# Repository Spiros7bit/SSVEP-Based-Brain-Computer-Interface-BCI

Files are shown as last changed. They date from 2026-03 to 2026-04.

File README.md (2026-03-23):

# SSVEP-Based Brain-Computer Interface

## Overview

This project implements a real-time Steady-State Visually Evoked Potential (SSVEP) Brain-Computer Interface (BCI) using an ESP32 microcontroller and a custom PCB for analog interface. It was developed as part of a thesis and demonstrates how EEG signals can be processed and classified in real time on embedded hardware.

The system detects brain responses to visual stimuli at specific frequencies and converts them into control decisions.

---

## System Architecture

The signal processing pipeline consists of the following stages:

1. **Analog Interface**
   
   * Instrumentation Amplifier
   * Low Pass Filter, Sallen Key, 2 order
   * AC amplifier
   * Notch 50 Hz filter
   * Final AC Amplifier
   * Right Leg Driver circuit
     
3. **Signal Acquisition**

   * ADC sampling at 1 kHz
   * Hardware timer interrupt for precise timing

4. **Preprocessing**

   * DC offset removal (IIR high-pass filter)
   * FIR band-pass filtering

5. **Feature Extraction**

   * Goertzel algorithm for frequency detection
   * Target frequencies: 10 Hz, 12 Hz, 20 Hz, 24 Hz

6. **Decision Making**

   * Argmax power comparison
   * Median Absolute Deviation (MAD)-based classifier

7. **Output**

   * Real-time signal visualization via Serial Plotter
   * Classification results (Argmax & MAD)

---

## Features

* Analog interface and Acquition System
* Real-time processing on ESP32
* 1 kHz sampling using hardware timer interrupts
* Efficient fixed-point DSP implementation
* FIR filtering with circular buffer
* Sliding window Goertzel analysis (with overlap)
* Robust classification using MAD
* Serial output for debugging and visualization

---

## Hardware Requirements

* ESP32 development board
* EEG acquisition circuit (as designed in the thesis)
* Electrodes and analog front-end

**ADC Input:** GPIO34 (ADC1_CHANNEL_6)

---

## Software Requirements

* Arduino IDE or PlatformIO
* ESP32 board support package

---

## How It Works

### Sampling

A hardware timer triggers ADC sampling at 1000 Hz. Each sample is processed in real time.

### DC Removal

A simple IIR filter removes the DC component from the signal:

```
dc_est = dc_est + k * (x - dc_est)
```

### FIR Filtering

A band-pass FIR filter is applied to isolate relevant EEG frequencies.

### Goertzel Algorithm

The Goertzel algorithm is used to compute the energy at specific target frequencies efficiently.

* Window size: 2048 samples
* Step size: 256 samples (overlap processing)

### Decision Logic

Two decision methods are implemented:

1. **Argmax**

   * Compares power between frequency groups

2. **MAD (Median Absolute Deviation)**

   * Computes a robust threshold based on signal statistics
   * Reduces noise and false detections

---

## Output Format

The system outputs data via Serial in the following format:

```
signal_value, argmax_decision, mad_decision
```

This can be visualized using the Arduino Serial Plotter.

---

## Project Structure

```
.
├── main.ino
├── fir_new_2_1000hz.h   # FIR filter coefficients
├── README.md
```

---

## Applications

* Brain-computer interfaces (BCI)
* Assistive technologies
* Neuroengineering research
* Real-time embedded DSP systems

---

## Future Improvements

* Add more target frequencies
* Improve classification accuracy
* Wireless data transmission (Bluetooth/WiFi)
* GUI for real-time monitoring
* Add a TinyML algorithm

---

## Author

Developed as part of a thesis project on SSVEP-based Brain-Computer Interfaces.

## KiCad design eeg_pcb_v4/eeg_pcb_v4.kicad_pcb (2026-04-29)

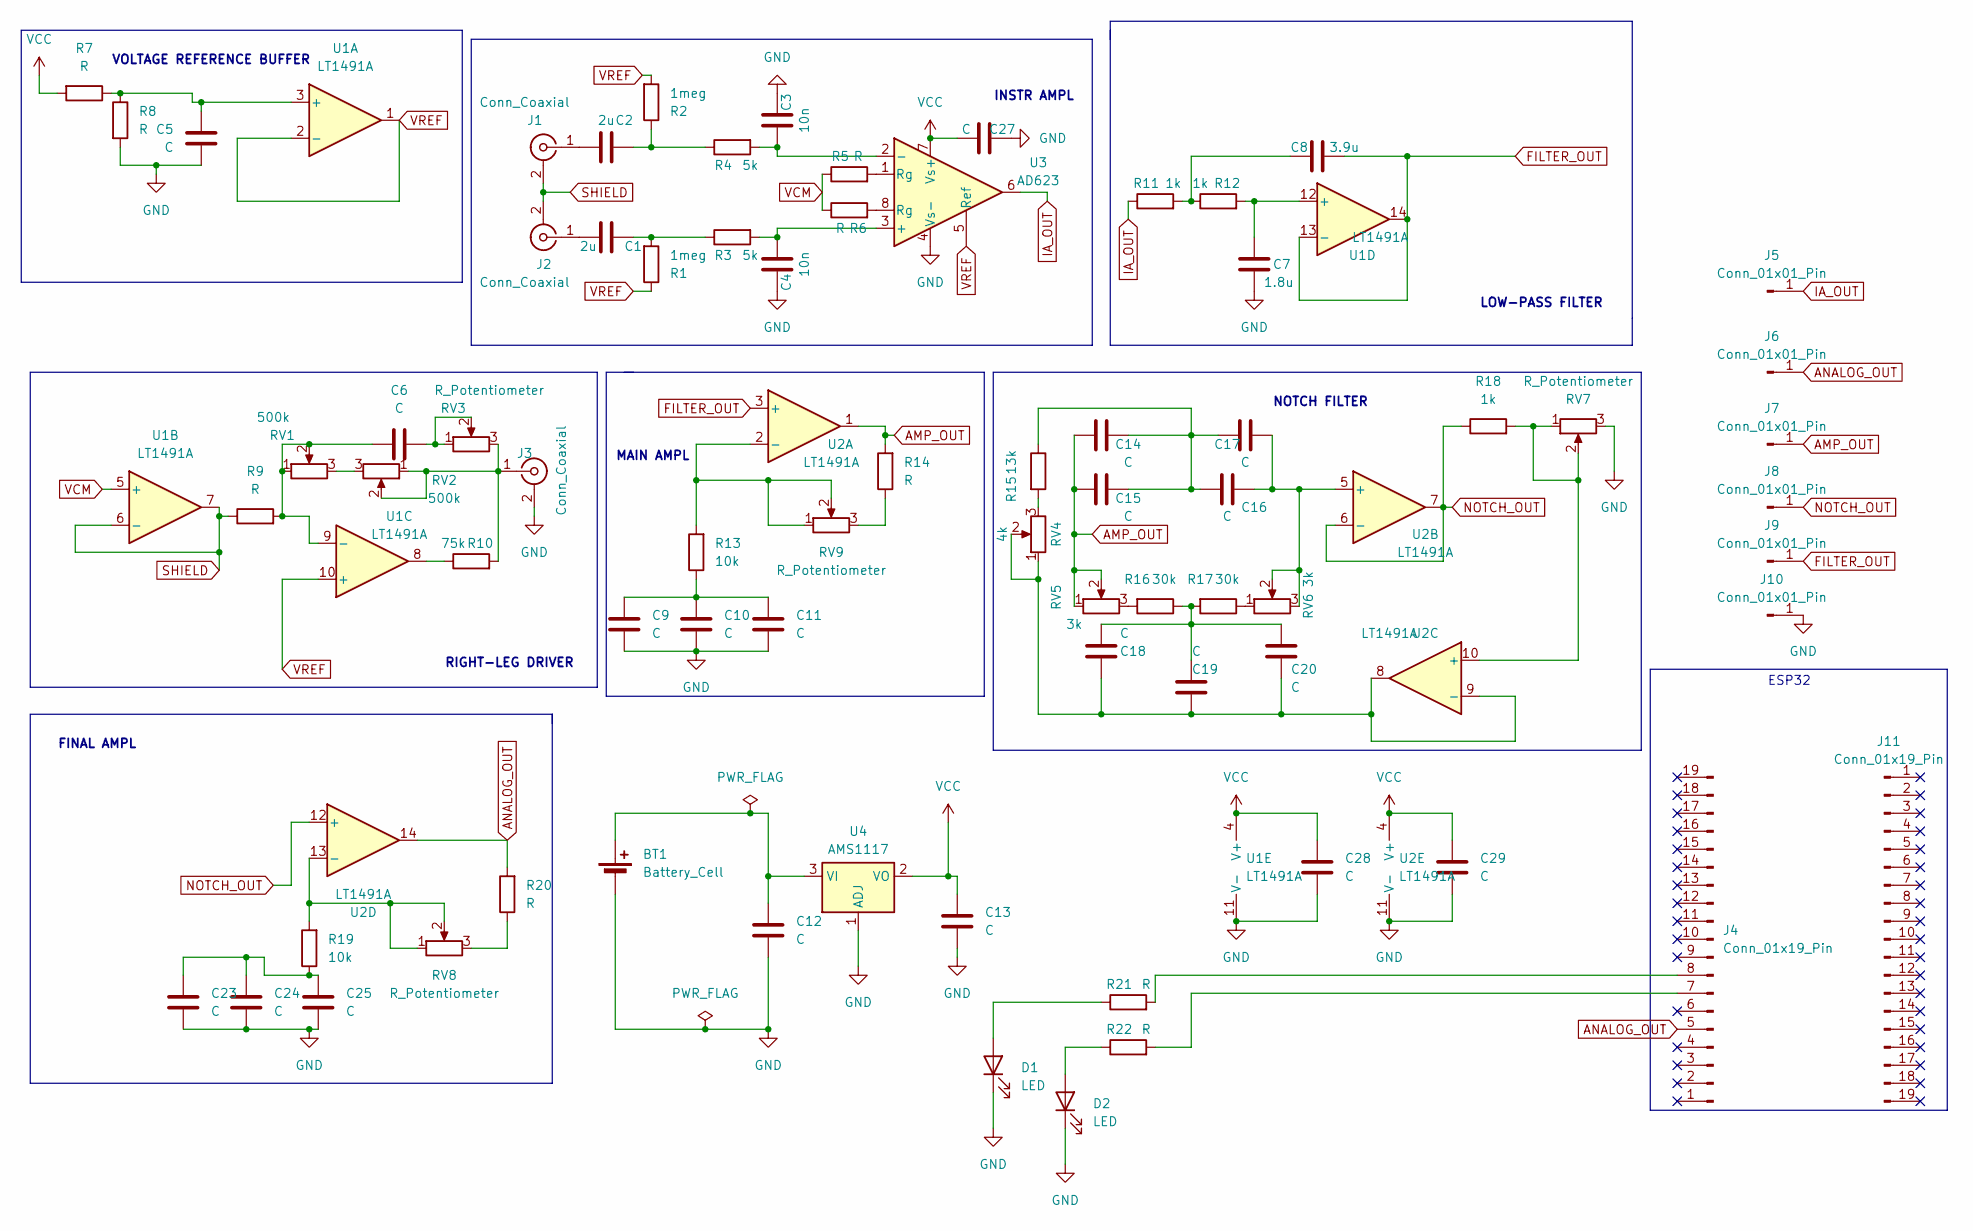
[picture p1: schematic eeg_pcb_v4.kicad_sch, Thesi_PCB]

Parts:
BT1: Battery_Cell; TerminalBlock_Altech_AK300-2_P5.00mm
C1, C2: 2u; C_1206_3216Metric
C3, C4: 10n; C_1206_3216Metric
C5, C6, C9, C10, C11, C12, C13, C14, C15, C16, C17, C18, C19, C20, C23, C24, C25, C27, C28, C29: C; C_1206_3216Metric
C7: 1.8u; C_1206_3216Metric
C8: 3.9u; C_1206_3216Metric
D1, D2: LED; LED_0805_2012Metric
J1, J2, J3: Conn_Coaxial; BNC_Amphenol_B6252HB-NPP3G-50_Horizontal
J4, J11: Conn_01x19_Pin; PinHeader_1x19_P2.54mm_Vertical
J5, J6, J7, J8, J9, J10: Conn_01x01_Pin; TestPoint_Pad_D1.0mm
R1, R2: 1meg; R_1206_3216Metric
R3, R4: 5k; R_1206_3216Metric
R5, R6, R7, R8, R9, R14, R20, R21, R22: R; R_1206_3216Metric
R10: 75k; R_1206_3216Metric
R11, R12, R18: 1k; R_1206_3216Metric
R13, R19: 10k; R_1206_3216Metric
R15: 13k; R_1206_3216Metric
R16, R17: 30k; R_1206_3216Metric
RV1, RV2: 500k; Potentiometer_Bourns_TC33X_Vertical
RV3, RV7, RV8, RV9: R_Potentiometer; Potentiometer_Bourns_TC33X_Vertical
RV4: 4k; Potentiometer_Bourns_TC33X_Vertical
RV5, RV6: 3k; Potentiometer_Bourns_TC33X_Vertical
U1, U2: LT1491A; SO-14_3.9x8.65mm_P1.27mm
U3: AD623; SO-8_3.9x4.9mm_P1.27mm
U4: AMS1117; SOT-223-3_TabPin2

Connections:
AMP_OUT: C14.1, C15.1, J7.1, R14.2, RV5.1, RV5.2, U2.1
ANALOG_OUT: J4.5, J6.1, R20.2, U2.14
FILTER_OUT: C8.2, J9.1, U1.13 (-), U1.14, U2.3 (+)
GND: BT1.2 (-), C3.1, C4.1, C5.2, C7.2, C9.2, C10.2, C11.2, C12.2, C13.2, C23.2, C24.2, C25.2, C27.2, C28.2, C29.2, D1.1 (K), D2.1 (K), J3.2 (Ext), J10.1, R8.2, RV7.3, U1.11 (V-), U2.11 (V-), U3.4 (Vs-), U4.1 (ADJ)
IA_OUT: J5.1, R11.1, U3.6
NOTCH_OUT: J8.1, R18.1, U2.6 (-), U2.7, U2.12 (+)
unnamed: BT1.1 (+), C12.1, U4.3 (VI)
unnamed: C1.2, R1.2, R3.1
unnamed: C2.2, R2.1, R4.1
unnamed: C6.2, RV3.1, RV3.2
unnamed: C8.1, R11.2, R12.1
unnamed: C9.1, C10.1, C11.1, R13.1
unnamed: C14.2, C15.2, C16.1, C17.1, R15.1
unnamed: C18.1, C19.1, C20.1, R16.1, R17.2
unnamed: C23.1, C24.1, C25.1, R19.1
unnamed: D1.2 (A), R21.1
unnamed: D2.2 (A), R22.1
unnamed: C2.1, J1.1 (In)
unnamed: C1.1, J2.1 (In)
unnamed: J3.1 (In), R10.2, RV2.1, RV2.2, RV3.3
unnamed: J4.7, R22.2
unnamed: J4.8, R21.2
unnamed: R5.2, U3.1 (Rg)
unnamed: R6.2, U3.8 (Rg)
unnamed: R10.1, U1.8
unnamed: R14.1, RV9.3
unnamed: R15.2, RV4.3
unnamed: R16.2, RV5.3
unnamed: R17.1, RV6.1
unnamed: R20.1, RV8.3
unnamed: RV1.3, RV2.3
unnamed: C5.1, R7.1, R8.1, U1.3 (+)
unnamed: C6.1, R9.2, RV1.1, RV1.2, U1.9 (-)
unnamed: C7.1, R12.2, U1.12 (+)
unnamed: R13.2, RV9.1, RV9.2, U2.2 (-)
unnamed: C16.2, C17.2, RV6.2, RV6.3, U2.5 (+)
unnamed: R18.2, RV7.1, RV7.2, U2.10 (+)
unnamed: C18.2, C19.2, C20.2, RV4.1, RV4.2, U2.8, U2.9 (-)
unnamed: R19.2, RV8.1, RV8.2, U2.13 (-)
unnamed: C4.2, R3.2, U3.3 (+)
unnamed: C3.2, R4.2, U3.2 (-)
SHIELD: J1.2 (Ext), J2.2 (Ext), R9.1, U1.6 (-), U1.7
VCC: C13.1, C27.1, C28.1, C29.1, R7.2, U1.4 (V+), U2.4 (V+), U3.7 (Vs+), U4.2 (VO)
VCM: R5.1, R6.1, U1.5 (+)
VREF: R1.1, R2.2, U1.1, U1.2 (-), U1.10 (+), U3.5 (Ref)

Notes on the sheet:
RIGHT-LEG DRIVER
LOW-PASS FILTER
NOTCH FILTER
ESP32
MAIN AMPL
INSTR AMPL
VOLTAGE REFERENCE BUFFER
FINAL AMPL

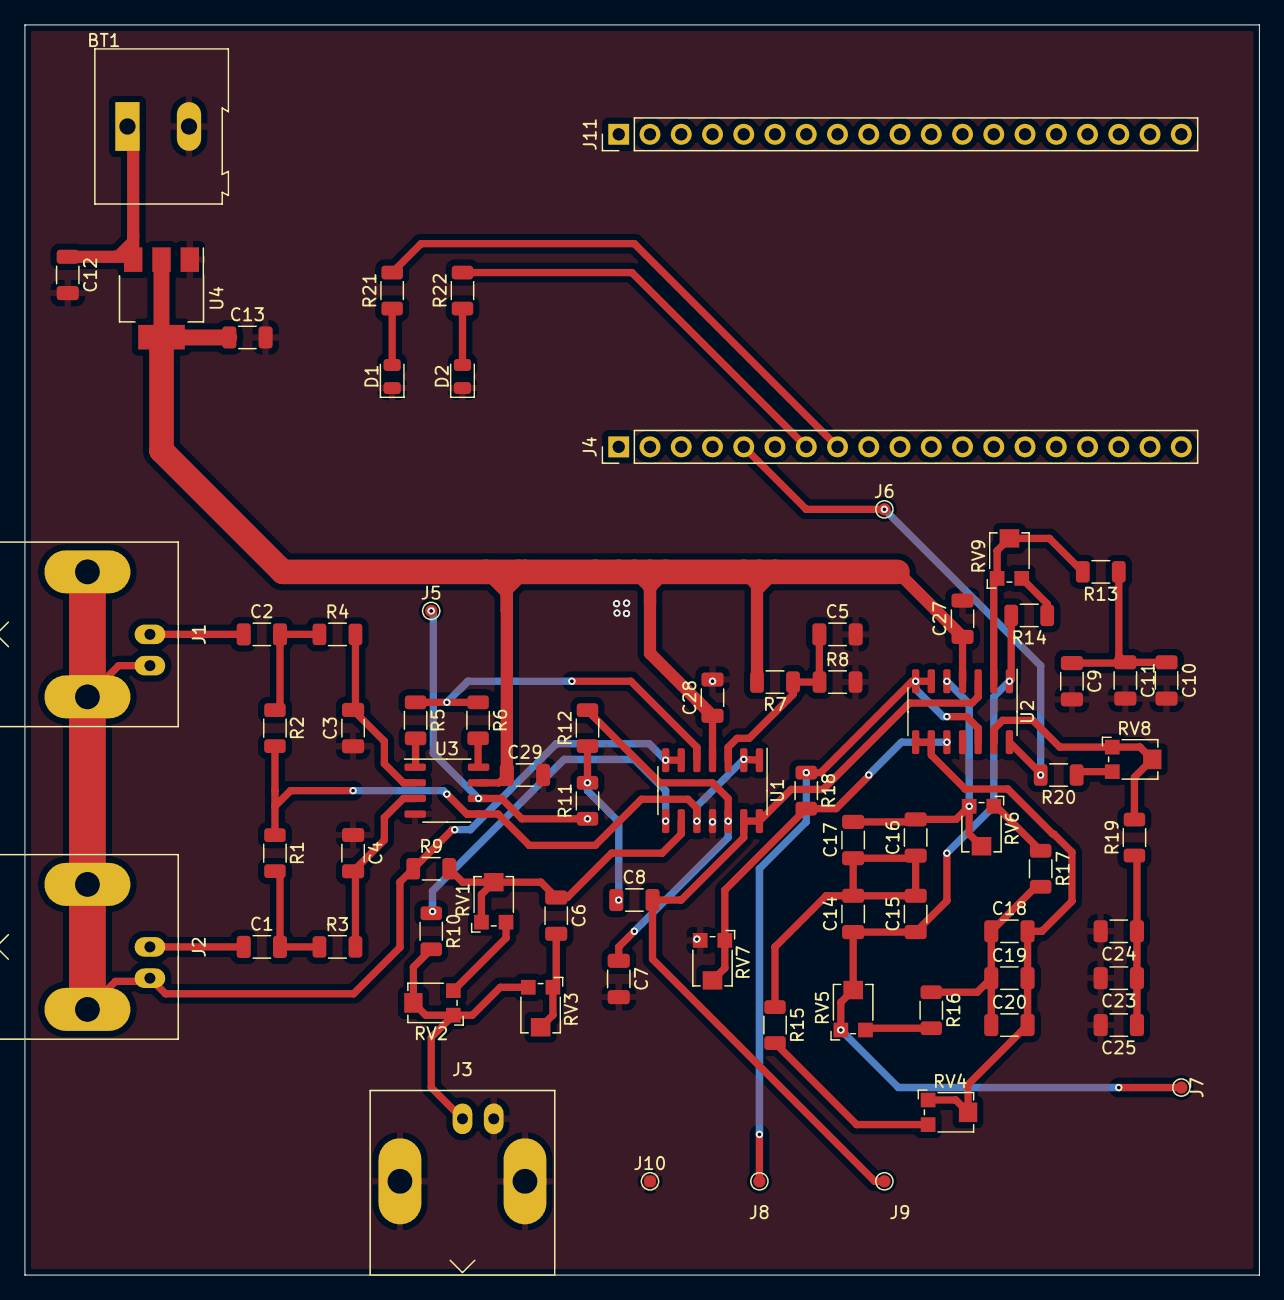
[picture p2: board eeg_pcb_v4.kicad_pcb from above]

Board: 2 copper layers, 100.3 x 101.6 mm, 75 parts (0 on the bottom side), 45 nets.

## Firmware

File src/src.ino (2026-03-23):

// ================= Libraries =================
#include <Arduino.h>
#include "driver/adc.h"
#include "fir_new_2_1000hz.h"
#include <math.h>

// ================= ΡΥΘΜΙΣΕΙΣ =================
#define SAMPLE_RATE         1000                // Sampling Frequency
#define ADC_CH              ADC1_CHANNEL_6      // GPIO34
#define DC_SHIFT            5                   // k = 1/32, for dc remover
#define GOERTZEL_N          2048                // Number of samples proccessed by Goertzel algorithm
#define GOERTZEL_STEP       256                 // Number of samlples for decision algorithm (overlap = GOERTZEL_N - GOERTZEL_STEP)
#define TH                  0.5f                // fixed threshold for decision

// --- Goertzel parameters ---
const int NUM_FREQ = 4; //number of computed frequencies
float target_freq[NUM_FREQ] = {10.0, 12.0, 20.0, 24.0}; 

// ================= TIMER ISR =================
hw_timer_t *timer = NULL;
volatile int16_t adcSample = 0;
volatile bool sampleReady = false;

void IRAM_ATTR onTimer()
{
    if (!sampleReady) {
        adcSample = (int16_t)adc1_get_raw(ADC_CH); //Channel 1 for ADC
        sampleReady = true; //Flag for ready sample
    }
}

void initTimer(){
    adc1_config_width(ADC_WIDTH_BIT_12); 
    adc1_config_channel_atten(ADC_CH, ADC_ATTEN_DB_11); //Input signal is in range (0-3V), so the attenuation is 11 dB

    timer = timerBegin(1000000);          // set the prescaler to 1MHz
    timerAttachInterrupt(timer, &onTimer);
    timerAlarm(timer, SAMPLE_RATE, true, 0); //set the interrupt timer to 1ms
}

// ================= DC REMOVER =================
int32_t dc_est = 0;   // init the dc the algorithm detects

inline int16_t removeDC(int16_t x)
{
    // x is 12-bit ADC (0-4095)
    // trnasfer the data to 32 bit data for better resolution on the next computes
    int32_t temp = x;

    // dc_est = dc_est + k*(x - dc_est)
    dc_est +=  (temp - dc_est) >> DC_SHIFT ; //accumulator

    // AC output
    int32_t y = (temp - dc_est);

    // saturation
    if (y > 32767) y = 32767;
    if (y < -32768) y = -32768;

    return (int16_t)y; //12 bit information to int16
}

// ================= FIR FILTER =================
static int16_t delayLine[coeffLen] = {0}; //delayLine buffer to store some previous data, so the fir filter has memory and doesnt reset every new porcess
static size_t firWriteIdx = 0;

inline int16_t FIR_processSample(int16_t x)
{

    delayLine[firWriteIdx] = x;

    int32_t acc = 0;
    size_t idx = firWriteIdx;

    for (size_t k = 0; k < coeffLen; k++) {
        acc += (int32_t)delayLine[idx] * (int32_t)coeff[k];
        idx = (idx == 0) ? coeffLen - 1 : idx - 1;
    }

    firWriteIdx++;
    if (firWriteIdx >= coeffLen)
        firWriteIdx = 0;

    // Q28 → Q12
    acc >>= (28 - 12);

    // Saturation (Q12)
    if (acc >  32768) acc =  32768;
    if (acc < -32768) acc = -32768;

    return (int16_t)acc;
}

// ================= GOERTZEL ALGORITHM =================
int32_t coeffGoertzel[NUM_FREQ];
//Goertzel algorithm is a 2 taps IIR filter, s1, s2 is the memory of filter
int32_t s1[NUM_FREQ] = {0};
int32_t s2[NUM_FREQ] = {0};

int goertzelCount = 0; // cycle data to compute the new result
int bufferIdx = 0;  //counter of goertzel algorithm resolution

int16_t goertzelBuffer[GOERTZEL_N] = {0};

// ================= INIT GOERTZEL =================
void initGoertzel() {
    for (int i = 0; i < NUM_FREQ; i++) {
        float omega = 2.0f * M_PI * target_freq[i] / SAMPLE_RATE;
        coeffGoertzel[i] = roundf(32767 * (2.0f * cosf(omega)));
        s1[i] = 0;
        s2[i] = 0;
    }
    goertzelCount = 0;
    bufferIdx = 0;
}

// ================= GOERTZEL ALGORITHM =================
void processGoertzelSampleStep(int16_t sample, int32_t mags[NUM_FREQ], bool &newResult) {
    newResult = false;

    goertzelBuffer[bufferIdx++] = sample;
    goertzelCount++;

    if (bufferIdx >= GOERTZEL_N)
        bufferIdx = 0;

    if (goertzelCount >= GOERTZEL_STEP) {

        for (int f = 0; f < NUM_FREQ; f++) {
            int32_t s1_local = 0;
            int32_t s2_local = 0;
            int32_t coeff = coeffGoertzel[f];

            for (int n = 0; n < GOERTZEL_N; n++) {
                int16_t x = goertzelBuffer[(bufferIdx + n) % GOERTZEL_N];
                int64_t prod = ((int64_t)coeff * s1_local) >> 15;
                int32_t s0 = x + (int32_t)prod - s2_local;
                s2_local = s1_local;
                s1_local = s0;
            }

            //use floating point numbers for better resolution
            float omega = 2.0f * M_PI * target_freq[f] / SAMPLE_RATE;
            float real = s1_local - cosf(omega) * s2_local;
            float imag = sinf(omega) * s2_local;
            mags[f] = (int32_t)sqrtf(real*real + imag*imag);
        }

        goertzelCount = 0;
        newResult = true; //flag for new result
    }
}

// ================= MAD DECISION =================
#define MAD_WIN 25 //Counter to compute the new MAD 
#define K_MAD   0.7f //Threashold for MAD classifier

float scoreBuffer[MAD_WIN]; 
int scoreIdx = 0;
int scoreCount = 0;

// helper for median
float computeMedian(float *arr, int n) {
    float temp[MAD_WIN];
    memcpy(temp, arr, n * sizeof(float));

    // simple insertion sort (n μικρό)
    for (int i = 1; i < n; i++) {
        float key = temp[i];
        int j = i - 1;
        while (j >= 0 && temp[j] > key) {
            temp[j+1] = temp[j];
            j--;
        }
        temp[j+1] = key;
    }

    if (n % 2 == 0)
        return 0.5f * (temp[n/2 - 1] + temp[n/2]);
    else
        return temp[n/2];
}

float computeMAD(float *arr, int n, float median) {
    float dev[MAD_WIN];
    for (int i = 0; i < n; i++)
        dev[i] = fabs(arr[i] - median); //Meadian = |x_i-Meadian(x)|

    return computeMedian(dev, n);
}


// ================= SETUP =====================
void setup()
{
    Serial.begin(921600);
    initTimer();
    //initHann();
    initGoertzel();
    //pinMode(22, OUTPUT);
    //pinMode(23, OUTPUT);
    
}


// ================= LOOP =================
int32_t mags[NUM_FREQ];
static int decisionArgmax = 0;
static int decisionMAD = 0;

void loop()
{
    if (sampleReady) {

        noInterrupts();
        int16_t x = adcSample;
        sampleReady = false;
        interrupts();

        int16_t x_ac = removeDC(x);
        int16_t y = FIR_processSample(x_ac);

        bool newResult = false;
        processGoertzelSampleStep(y, mags, newResult);

        if (newResult) {
            float power0 = (float)mags[0]*mags[0] + (float)mags[2]*mags[2];
            float power1 = (float)mags[1]*mags[1] + (float)mags[3]*mags[3];

            float score = logf(power1 + 1.0f) - logf(power0 + 1.0f);

            // update scoreBuffer
            scoreBuffer[scoreIdx++] = score;
            if (scoreIdx >= MAD_WIN) scoreIdx = 0;
            if (scoreCount < MAD_WIN) scoreCount++;

            // argmax
            decisionArgmax = (power1 > power0) ? 1 : 0;

            // MAD (computes the MAD for MAD_WIN=25 samples, but wait for the first)
            if (scoreCount >= 5) { // Wait for buffer to collect the first 5 samples, for more statistical stability 
                float med = computeMedian(scoreBuffer, scoreCount);
                float mad = computeMAD(scoreBuffer, scoreCount, med);

                if (score > med + K_MAD * mad)
                    decisionMAD = (score > 0) ? 1 : 0;
                else if (score < med - K_MAD * mad)
                    decisionMAD = (score > 0) ? 1 : 0;
                // αλλιώς κράτα το lastDecisionMAD
            }

        }

        // Output κάθε sample για να βλέπεις το σήμα στο Serial Plotter
        float vout = y * (3.3f / 4095.0f);
        Serial.print(vout, 3);
        Serial.print(",");
        Serial.print(decisionArgmax);
        Serial.print(",");
        Serial.println(decisionMAD);
    }
}
